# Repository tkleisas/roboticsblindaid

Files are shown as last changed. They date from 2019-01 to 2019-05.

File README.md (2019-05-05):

# roboticsblindaid
Σύστημα Ειδοποίησης Ατόμων με Προβλήματα Όρασης

Πρωτότυπο #1

Παρουσίαση του Project με βίντεο
================================
https://www.youtube.com/watch?v=oLjfnk1CDiU

Υλικά
=====
1. Αισθητήρας Υπερήχων HC-SR04 https://grobotronics.com/ultrasonic-sensor-sr04.html
2. Βύσματάκι για ακουστικά 3.5mm https://grobotronics.com/audio-jack-stereo-3.5mm-pcb.html
3. 2 ή περισσότερα micro:bit https://grobotronics.com/bbc-micro-bit-board.html
4. Boost converter για τη μετατροπή της τάσης από τα 3V που θα παρέχουν οι μπαταρίες στα 5V που απαιτεί ο αισθητήρας https://grobotronics.com/pololu-dc-dc-converter-step-up-5v-1.2a.html
5. Logic level converter για τη μετατροπή των τάσεων μεταξύ 3V και 5V έτσι ώστε να μπορούν να επικοινωνήσουν ο αισθητήρας υπερήχων που δουλεύει στα 5V με το microbit που δουλεύει στα 3V. https://grobotronics.com/logic-level-converter-bi-directional.html   
5. Μπαταριοθήκες https://grobotronics.com/battery-holder-2xa-with-jst-ph-connector.html
6. Perfboard για να συναρμολογήσουμε το κύκλωμά μας https://grobotronics.com/160x115mm.html
7. Μονόκλωνο καλώδιο σε διάφορα χρώματα για να κάνουμε τις συνδέσεις https://grobotronics.com/prototyping/hook-up-wires/
8. Pin header για την προσαρμογή του αισθητήρα υπερήχων στην πλακέτα! https://grobotronics.com/pin-header-1x40-female-2.54-mm.html
Προαιρετικά:
μοτέρ και Motor Driver Board για ειδοποίηση με δόνηση

Το σύστημα αυτό θα βοηθήσει τους ανθρώπους που έχουν προβλήματα όρασης να δουν τα εμπόδια που είναι πιο ψηλά από το μπαστούνι που έχουν για να κινηθούν. Μπορούμε να έχουμε αισθητήρες στο στήθος και στο κεφάλι (σε καπέλο) Ο αισθητήρας υπερήχων όταν ανιχνεύει κάποιο εμπόδιο θα κάνει τα ακουστικά να παράγουν έναν προειδοποιητικό ήχο, ώστε ο χρήστης του συστήματος να καταλάβει ότι έχει κάποιο εμπόδιο μπροστά του. Επίσης θα μπορούσαμε να χρησιμοποιήσουμε και κάποιο μοτέρ για ειδοποίηση. Θα χρησιμοποιηθούν 2 micro:bit, το ένα θα ανιχνεύει την κίνηση και θα στέλνει ασύρματα μήνυμα στο άλλο για να παράγει την ειδοποίηση. Τρόποι ειδοποίησης μπορεί να είναι τονικό ύψος του ήχου ανάλογα με την απόσταση ή επαναλήψεις του ήχου αντιστρόφος ανάλογες της απόστασης, ή κάποια μελωδία ή κάποια δόνηση παραγόμενη από το μοτέρ

Μπορούμε να δούμε στο επόμενο διάγραμμα μια ενδεικτική υλοποίηση ενός τέτοιου συστήματος που περιλαμβάνει μπαταρίες, ένα micro:bit, έναν αισθητήρα υπερήχων και έναν DC - DC boost converter. Επειδή το micro:bit θέλει 3 Volts, ενώ ο αισθητήρας χρειάζεται 5 Volts, χρησιμοποιούμε τον boost converter για να πάρουμε 5 Volts από τις δυο μπαταρίες ΑΑΑ που δίνουν 3 Volts. Με αυτό τον τρόπο μπορούμε να κάνουμε πιο μικρό και πιο ελαφρύ το κύκλωμά μας, πράγμα που είναι απαραίτητο για μια συσκευή που πρέπει να φοριέται. Θα μπορούσαμε να χρησιμοποιήσουμε ακόμη και μια μικρή, στρογγυλή μπαταρία λιθίου 3V (πχ CR2032) για ακόμη πιο μικρή συσκευή. Τέλος υπάρχει και ένα 3.5 mm jack στο οποίο μπορούμε να συνδέσουμε ακουστικό ώστε να έχουμε ηχητική ειδοποίηση.
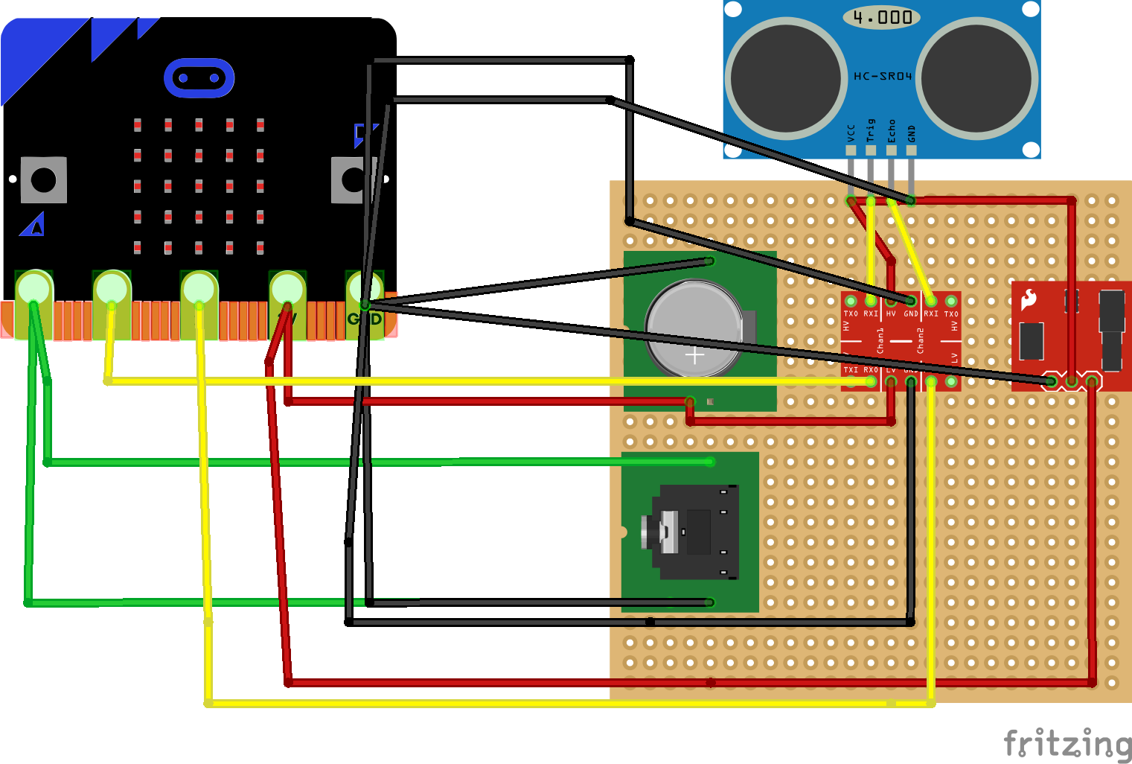
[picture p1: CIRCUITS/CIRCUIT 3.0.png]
Micro:bit and ultrasonic sensor

Μπορείτε να δείτε επίσης μερικές φωτογραφίες από την δοκιμαστική υλοποίηση που κάναμε.
Πλακέτα από πάνω

Πλακέτα από κάτω

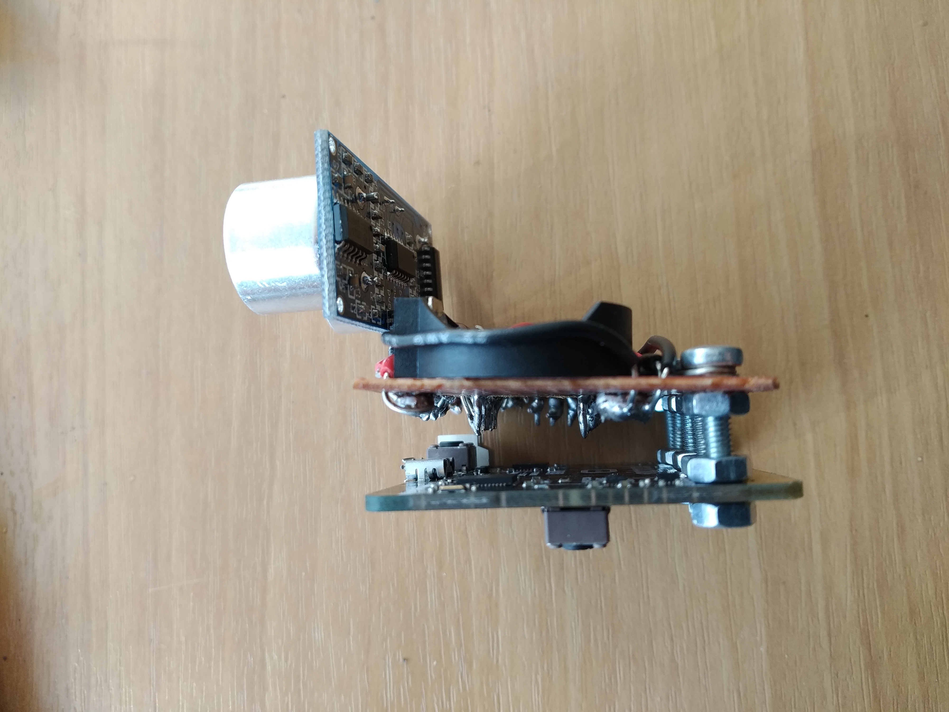
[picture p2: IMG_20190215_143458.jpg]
Πλακέτα από πλάϊ


Στον πάγκο εργασίας

Πατήστε εδώ για να δείτε το βίντεο με το πρωτότυπο.
https://youtu.be/QQmOa1Lk4nE

Επίσης στο φάκελο 3dprint μπορείτε να βρείτε σχέδια για ένα περίβλημα της συσκευής που σχεδιάσαμε στο openscad

Λίγα λόγια για την υλοποίηση του έργου
======================================

Στο κέντρο ρομποτικής και προγραμματισμού Καλαμάτας (που στελεχώνεται από εθελοντές εκπαιδευτικούς του Δημόσιου Σχολείου) ξεκινήσαμε φέτος μια σειρά μαθημάτων πάνω στις ανοιχτές τεχνολογίες.
Σκοπός μας ήταν να ξεκινήσουμε με το micro:bit και να συνεχίσουμε με Arduino και Raspberry pi. Όταν ανακοινώθηκε ο διαγωνισμός εκπαιδευτικής ρομποτικής και physical computing ανοιχτών τεχνολογιών της ΕΛΛΑΚ είχαμε σχεδόν ολοκληρώσει μια εισαγωγική σειρά μαθημάτων στο micro:bit και αποφασίσαμε να προτείνουμε ένα έργο που βρήκαμε ενδιαφέρον. Μια συσκευή ειδοποίησης ατόμων με προβλήματα όρασης. Το θέμα αυτό ήταν ελκυστικό γιατί αναφερόταν σε ένα υπαρκτό πρόβλημα, ενώ παράλληλα μπορεί να ευαισθητοποιήσει και να κινητοποιήσει τους μαθητές να καταλάβουν τα προβλήματα κάποιων συνανθρώπων τους και να προσπαθήσουν να τους βοηθήσουν. Παράλληλα μέσα από την ενασχόλησή τους αυτή, θα είχαν την ευκαιρία να γνωρίσουν κάποιες βασικές αρχές του physical computing, του προγραμματισμού, να σχεδιάσουν μια κατάλληλη διεπαφή έτσι ώστε οι χρήστες να μπορούν να χρησιμοποιήσουν τη συσκευή κ.ο.κ.

Αφού κάναμε αρκετές συζητήσεις για το πως θα μπορούσε να δουλέψει μια συσκευή και τους περιορισμούς που θα μπορούσε να έχει, δοκιμάσαμε μια αρχική υλοποίηση σε breadboard ενός κυκλώματος που περιελάμβανε έναν αισθητήρα υπερήχων, ένα micro:bit και τροφοδοσία του αισθητήρα από 4 επαναφορτιζόμενες μπαταρίες των 1,2 Volt (4,8 Volt) και ξεχωριστή τροφοδοσία για το micro:bit. Είδαμε ότι η χρήση 2 πηγών τροφοδοσίας δεν ήταν πρακτική και το σύστημα που προέκυπτε ήταν μεγάλο. Έτσι στη συνέχεια αποφασίσαμε να δούμε τη δυνατότητα να χρησιμοποιήσουμε ένα πιο απλό σχήμα τροφοδοσίας. Τελικά αποφασίσαμε να χρησιμοποιήσουμε έναν DC boost converter, ο οποίος θα έπαιρνε μια τάση τροφοδοσίας 3 Volts του micro:bit και θα την ανέβαζε στα 5 που χρειαζόταν για να δουλέψει ο αισθητήρας υπερήχων. Όμως είδαμε ότι η τάση που έστελνε το micro:bit για να κάνει τον αισθητήρα να στείλει τον υπερηχητικό παλμό μερικές φορές δεν τον ενεργοποιούσε. Παράλληλα χρησιμοποιούσαμε έναν διαιρέτη τάσης στο pin εξόδου για να μετατρέψουμε τα 5 volts που γύρναγε ο αισθητήρας σε 3V έτσι ώστε να μην υπάρχει πρόβλημα με το micro:bit. Έτσι τελικά αποφασίσαμε να χρησιμοποιήσουμε έναν logic level converter, ο οποίος μας επέτρεψε να δουλέψουμε χωρίς πρόβλημα καθώς έκανε δυνατή την μετατροπή των τάσεων από τα 3Volts στα 5Volts και αντίστροφα. Με αυτές τις αλλαγές το κύκλωμά μας δούλευε. Όμως επειδή ήταν σε breadboard ήταν πολύ εύθραυστο και δεν θα μπορούσε να χρησιμοποιηθεί για τη δημιουργία ενός πρωτοτύπου. Για αυτό το λόγο αποφασίσαμε να φτιάξουμε το σύστημά μας σε πλακέτα (perfboard) και να συνδέσουμε τα διάφορα μέρη με καλώδια. Οι μαθητές είδαν τη διαδικασία της κόλλησης σε μια πλακέτα με κολλητήρι και δοκίμασαν κάποιες απλές κολλήσεις. Όμως τελικά το πρωτότυπο κατασκευάστηκε στο εργαστήριό μας. Το πρώτο - πρώτο που φτιάχτηκε δε δούλεψε καν. Στη συνέχεια όμως η δεύτερη δοκιμή ήταν επιτυχημένη.

Προγραμματίσαμε τη συσκευή στο περιβάλλον make:code. Ο προγραμματισμός έγινε από τους μαθητές, οι οποίοι χρησιμοποίησαν και διαφορετικούς ήχους προκειμένου να βοηθήσουν το χρήστη να ρυθμίσει την απόσταση ειδοποίησης της συσκευής.

Στο μεταξύ η πρότασή μας πήρε χρηματοδότηση από την ΕΛΛΑΚ, οπότε μπορέσαμε να φτιάξουμε άλλα 3 πρωτότυπα, εφαρμόζοντας αυτά που μάθαμε από το πρώτο πρωτότυπο. Στη συνέχεια έπρεπε να βάλουμε την πλακέτα μας σε ένα κουτί. Για το σκοπό αυτό διαθέταμε έναν επιτραπέζιο εκτυπωτή PrimaCreator p120 v3. Αρχικά είπαμε κάποια πράγματα για την τρισδιάστατη εκτύπωση και το πως δουλεύει και στη συνέχεια δοκιμάσαμε να σχεδιάσουμε ένα κουτί στο tinkercad. Το τελικό κουτί φτιάχτηκε με το πρόγραμμα OpenScad το οποίο έχει το πλεονέκτημα ότι είναι open source και ότι φτιάχνει τρισδιάστατα μοντέλα με μια γλώσσα προγραμματισμού! Αφού σχεδιάσαμε το κουτί, κάναμε μια δοκιμαστική εκτύπωση, διορθώσαμε κάποιες διαστάσεις και κάναμε μια εκτύπωση του κουτιού. Παρόλες τις διορθώσεις, υπήρχαν μερικά προβλήματα που διορθώθηκαν με λίμα και γυαλόχαρτο. Οι μαθητές δεν είδαν την διαδικασία εκτύπωσης ζωντανά, αλλά από βίντεο και timelapse,
γιατί ο εκτυπωτής δεν ήταν στο χώρο που κάναμε μάθημα. Η εκτύπωση της θήκης πήρε γύρω στις 18 ώρες και την έχουμε τεκμηριώσει με σχετικά βίντεο.

Στη συνέχεια κουμπώσαμε τη συσκευή μας στο κουτί και κάναμε κάποιες δοκιμές. Η συσκευή μας δουλεύει, χρειάζεται όμως δουλειά πάνω στην εργονομία, πράγμα που διαπιστώσαμε και με τις δοκιμές. Κάτι που παραλείψαμε είναι ένα ρυθμιστικό της έντασης ειδοποίησης της συσκευής και ενδεχομένως κάποιο ενσωματωμένο ηχείο, έτσι ώστε να μη χρειάζονται ακουστικά.

Δεν προλάβαμε να υλοποιήσουμε την χρήση περισσότερων από ένα micro:bit για την ειδοποίηση. 

Στο μέλλον θα θέλαμε να εξετάσουμε και τη χρήση άλλων πλατφορμών, όπως το Arduino για την υλοποίηση της συσκευής μας, καθώς και το ενδεχόμενο η συσκευή μας να επικοινωνεί με το κινητό του χρήστη και να συνδιάζει και πληροφορίες από το κινητό για να τον βοηθάει να κινηθεί.

Τα μέλη της ομάδας μας είναι (αλφαβητικά):

Παναγιώτης Ξαρχάκος
Γιώργος Κωνσταντόπουλος
Γιώργος Τριανταφυλλάκης

Εμψυχωτές - συμβουλάτορες:

Τάσος Κλείσας
Παναγιώτης Μελιγαλιώτης
Βασίλης Μιχαλόπουλος

Διάθεση του περιεχομένου
========================

Ο κώδικας του έργου διατίθεται με άδεια GPL v3.0

Το περιεχόμενο του έργου διατίθεται με άδεια Creative Commons Αναφορά Δημιουργού 4.0 Διεθνές.

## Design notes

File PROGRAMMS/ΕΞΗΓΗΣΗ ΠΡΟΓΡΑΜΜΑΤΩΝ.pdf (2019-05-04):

### ΕΞΗΓΗΣΗ ΠΡΟΓΡΑΜΜΑΤΩΝ

ΧΡΟΝΟΛΟΓΙΚΗ ΣΕΙΡΑ
BEEPER

Ένα απλό πρόγραμμα που ο ήχος που παράγεται μοιάζει με beeper από αυτοκίνητο όταν κάνει όπισθεν. Έχουμε μία μεταβλητή, η οποία μπορεί να αυξομειωθεί από τα κουμπιά Α και Β του micro:bit και ανάλογα την τιμή της μεταβλητής παράγεται ο αντίστοιχος ήχος.

PROGRAMM 1.0

Το πρόγραμμα αυτό παίρνει τιμές από έναν ultrasonic sensor και μας παρουσιάζει την τιμή στην οθόνη του micro:bit.

PROGRAMM 2.0

Σε αυτό το πρόγραμμα το micro:bit δείχνει με την βοήθεια της επέκτασης greek-led beta και Sonar στην LED 5*5 οθόνη του την μέση τιμή 5 τιμών που παίρνει ο αισθητήρας υπερήχων

PROGRAMM 3.0

Ενώσαμε λοιπόν το πρόγραμμα BEEPER με το PROGRAMM 2.0, ώστε να αναπαράγεται ήχος ανάλογα με το τι βλέπει ο αισθητήρας και όχι ότι του βάζουμε εμείς πατώντας τα κουμπιά Α και Β.

PROGRAMM NOTES 1.0

Ο Ultrasonic Sensor μετράει την απόσταση την οποία δείχνει στην οθόνη LED του micro:bit και αν η τιμή βρίσκεται ανάμεσα στις τιμές 100 και 80 θα παίζει μία νότα, όταν είναι ανάμεσα σε 80 και 60 μία πιο ψηλή νότα, κοκ.

PROGRAMM NOTES 2.0

Παρατηρήσαμε ότι οι τιμές που βγάζει στην οθόνη το micro:bit δεν είναι σταθερές και για να σταθεροποιήσουμε αυτή τη τιμή φτιάξαμε μία συνάρτηση με την οποία ο Ultrasonic Sensor θα παίρνει πολλές τιμές και στην οθόνη θα δείχνει μία μέση τιμή, αυτό θα βοηθήσει και στην καλύτερη ειδοποίηση του ατόμου με το πρόβλημα όρασης

PROGRAMM NOTES 2.1

Σκεφτήκαμε πως τα άτομα με προβλήματα όρασης μπορεί να μην θέλουν να ειδοποιούνται από τα 100 cm αλλά από τα 80 ή από τα
200. Αυτό το καταφέραμε ρωτώντας στην αρχή τον χρήστη να μας δώσει μία τιμή, την οποία ο χρήστης μπορεί να αυξομειώσει με τα κουμπιά Α και Β. Όμως, επειδή οι χρήστες δεν θα μπορούν να βλέπουν τον αριθμό στην οθόνη, κάθε φορά που αλλάζει αυτός ο αριθμός θα ακούγεται ένα beat ανάλογα την τιμή που δίνεται (10cm 1 beat, 20cm 2 beat, κοκ).

PROGRAMM NOTES 2.2

Το micro:bit θα μπορεί πια να στέλνει την τιμή που παίρνει ο αισθητήρας υπερήχων σε μία οθόνη LCD η οποία θα δείχνει τον ίδιο αριθμό που φαίνεται και στην 5Χ5 οθόνη του micro:bit που χρησιμοποιεί ο χρήστης. Την οθόνη αυτή την χρησιμοποιούμε εμείς για να βλέπουμε τι τιμές παίρνει το micro:bit χωρίς να χρειάζεται να κοιτάμαι την οθόνη του χρήστη. Το πρόγραμμα που λαμβάνει την τιμή και το οποίο περνάμε στο micro:bit της LCD οθόνης έχει όνομα: "PROGRAMM NOTES LCD EDITION"

PROGRAMM LCD EDITION

Αυτό το πρόγραμμα το περνάμε στο micro:bit που έχει την LCD οθόνη. Με τη βοήθειά του λαμβάνει την τιμή που στέλνει το άλλο micro:bit.

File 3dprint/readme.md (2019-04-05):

Σε αυτό το φάκελο μπορείτε να βρείτε ένα σχέδιο περιβλήματος για την κατασκευή μας. Το σχέδιο έγινε με το λογισμικό ανοιχτού κώδικα openscad.
Ουσιαστικά είναι ένα πρόγραμμα το οποίο μπορεί να παράξει αρχεία STL τα οποία μπορούμε να εκτυπώσουμε αφού πρώτα τα εισάγουμε σε ένα πρόγραμμα slicer, όπως για παράδειγμα το CURA

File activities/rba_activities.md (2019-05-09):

Robotics Blind Aid
Περίγραμμα εκπαιδευτικών σεναρίων

1.	Εισαγωγή. Η σκοτεινή χώρα.

Για κάποιους συνανθρώπους μας η αίσθηση της όρασης απουσιάζει ή είναι πολύ περιορισμένη. Κάποιοι γεννήθηκαν έτσι, σε κάποιους έτυχε κατά τη διάρκεια της ζωής τους. Θα μπορούσε να συμβεί στον καθένα μας. Φυσικά οι άνθρωποι αυτοί ζουν με το πρόβλημά τους. Έχουν μάθει να εκμεταλλεύονται τις υπόλοιπες αισθήσεις τους με σκοπό να μπορούν να λειτουργήσουν στην κοινωνία. Πολλοί από αυτούς εργάζονται κανονικά. Πως είναι όμως να ζει κάποιος με πρόβλημα όρασης;

Βιωματική δραστηριότητα.
Δένουμε τα μάτια των μαθητών και τους αφήνουμε να περιπλανηθούν στον χώρο που περιέχει διάφορα εμπόδια (καρέκλες, θρανία κλπ). Αφού δοκιμάσουν όλοι, τους δίνουμε ένα μπαστούνι. Συζητάμε για το αν ήταν πιο εύκολη ή πιο δύσκολη η κίνηση με το μπαστούνι. Συζητάμε για τα πλεονεκτήματα και τα μειονεκτήματα του μπαστουνιού και τις εναλλακτικές που τυχόν γνωρίζουμε (πχ. Σκύλος οδηγός τυφλών). Συζητάμε για το πως η τεχνολογία μπορεί να βοηθήσει άτομα που αντιμετωπίζουν προβλήματα υγείας. Για παράδειγμα, η σύνθεση φωνής που χρησιμοποιούσε ο Stephen Hawking και του επέτρεπε να επικοινωνεί παρόλη την πάθηση (ALS) από την οποία έπασχε.

2.	Physical computing. Οι υπολογιστές αντιλαμβάνονται τον κόσμο.

Εμείς οι άνθρωποι διαθέτουμε αισθήσεις με τις οποίες αντιλαμβανόμαστε τον κόσμο. Με αυτές τις αισθήσεις, βρίσκουμε το δρόμο μας, αναζητούμε τροφή, μαθαίνουμε καινούρια πράγματα, προφυλασσόμαστε από τον κίνδυνο. Δεν υπάρχει ανθρώπινη δραστηριότητα στην οποία να μην εμπλέκονται μία ή περισσότερες αισθήσεις. Οι υπολογιστές μπορούν άραγε να αποκτήσουν αισθήσεις και να αντιληφθούν το περιβάλλον;
Συζήτηση με τους μαθητές. Παραδείγματα.
Οι υπολογιστές μπορούν να εξοπλιστούν με αισθητήρες. Ένας αισθητήρας μπορεί εκμεταλλευόμενος τους νόμους της φυσικής να αντιληφθεί φυσικά μεγέθη και να τα μετατρέψει σε αριθμούς κατάλληλους για επεξεργασία από έναν υπολογιστή. Παραδείγματα: επιταχυνσιόμετρο κινητού, συναγερμός, αισθητήρας παρκαρίσματος. Θα μπορούσαμε να χρησιμοποιήσουμε έναν ή περισσότερους αισθητήρες για να βοηθήσουμε άτομα με προβλήματα όρασης να αντιληφθούν καλύτερα το περιβάλλον τους.

3.	Micro:bit, ένας υπολογιστής με πολλές δυνατότητες.
Το micro:bit είναι ένας υπολογιστής σε μορφή πλακέτας ο οποίος διαθέτει πολλές δυνατότητες. Μπορεί να συνδεθεί εύκολα με αισθητήρες και μας επιτρέπει να φτιάξουμε διασκεδαστικές εφαρμογές όπως παιχνίδια, χρήσιμα εργαλεία (π.χ. πυξίδα), ρομποτικά οχήματα κ.ο.κ. Στο micro:bit μπορούμε να ξεκινήσουμε με δραστηριότητες όπως αυτές που περιγράφονται εδώ:
 https://4dimkal-robot.weebly.com/epsilonkappapialphaiotadeltaepsilonupsilontauiotakappa941sigmaf-deltarhoalphasigmatauetarhoiota972tauetatauepsilonsigmaf.html 
ή εδώ:
http://giamiaxoufta.blogspot.com/2018/10/microbit.html
Με σκοπό να εξοικειωθούν οι μαθητές με το micro:bit

4.	Σύνδεση ενός αισθητήρα υπερήχων με το micro:bit.
 Ο αισθητήρας υπερήχων μας επιτρέπει να μετράμε απόσταση. Δουλεύει στέλνοντας έναν υπερηχητικό παλμό ο οποίος αν συναντήσει εμπόδιο αντανακλάται και επιστρέφει πίσω. Ό χρόνος που μεσολαβεί από τη στιγμή που στείλουμε τον παλμό μέχρι τη στιγμή που θα ανιχνεύσουμε την αντανάκλασή του αντιστοιχεί στο διπλάσιο της  απόστασης από το αντικείμενο. Γνωρίζοντας και την ταχύτητα του ήχου στον αέρα μπορούμε να προσδιορίσουμε την απόσταση από το εμπόδιο. Με αυτό τον τρόπο λειτουργούν και τα δελφίνια και οι νυχτερίδες και γενικότερα όλα τα πλάσματα που χρησιμοποιούν ηχοεντοπισμό. Αντίστοιχα τέτοιες διατάξεις χρησιμοποιούμε στα σόναρ, τους αισθητήρες παρκαρίσματος κ.ο.κ. Βλέπουμε έναν τέτοιον αισθητήρα (HC-SR04) και ανακαλύπτουμε πως δουλεύει. Προσπαθούμε να τον συνδέσουμε με το micro:bit και ανακαλύπτουμε ότι ο συγκεκριμένος έχει κάποιες απαιτήσεις σε τάση που δεν μπορούν να καλυφθούν από το micro:bit. Δοκιμάζουμε πάντως τη σύνδεση με το micro:bit και έναν διαιρέτη τάσης για να μετατρέψουμε την τάση που επιστρέφει ο αισθητήρας από 5Volt σε 3Volt. Εξηγούμε την πολύπλοκη συνδεσμολογία μπαταρίας που απαιτείται.
5.	Σύνδεση ενός αισθητήρα υπερήχων μέρος β

6.	Προγραμματισμός του αισθητήρα για ειδοποίηση

7.	Πλακέτες

8.	Κουτί – 3D printing μέρος 1

9.	Κουτί – 3D printing μέρος 2

10.	Δοκιμές του συστήματος

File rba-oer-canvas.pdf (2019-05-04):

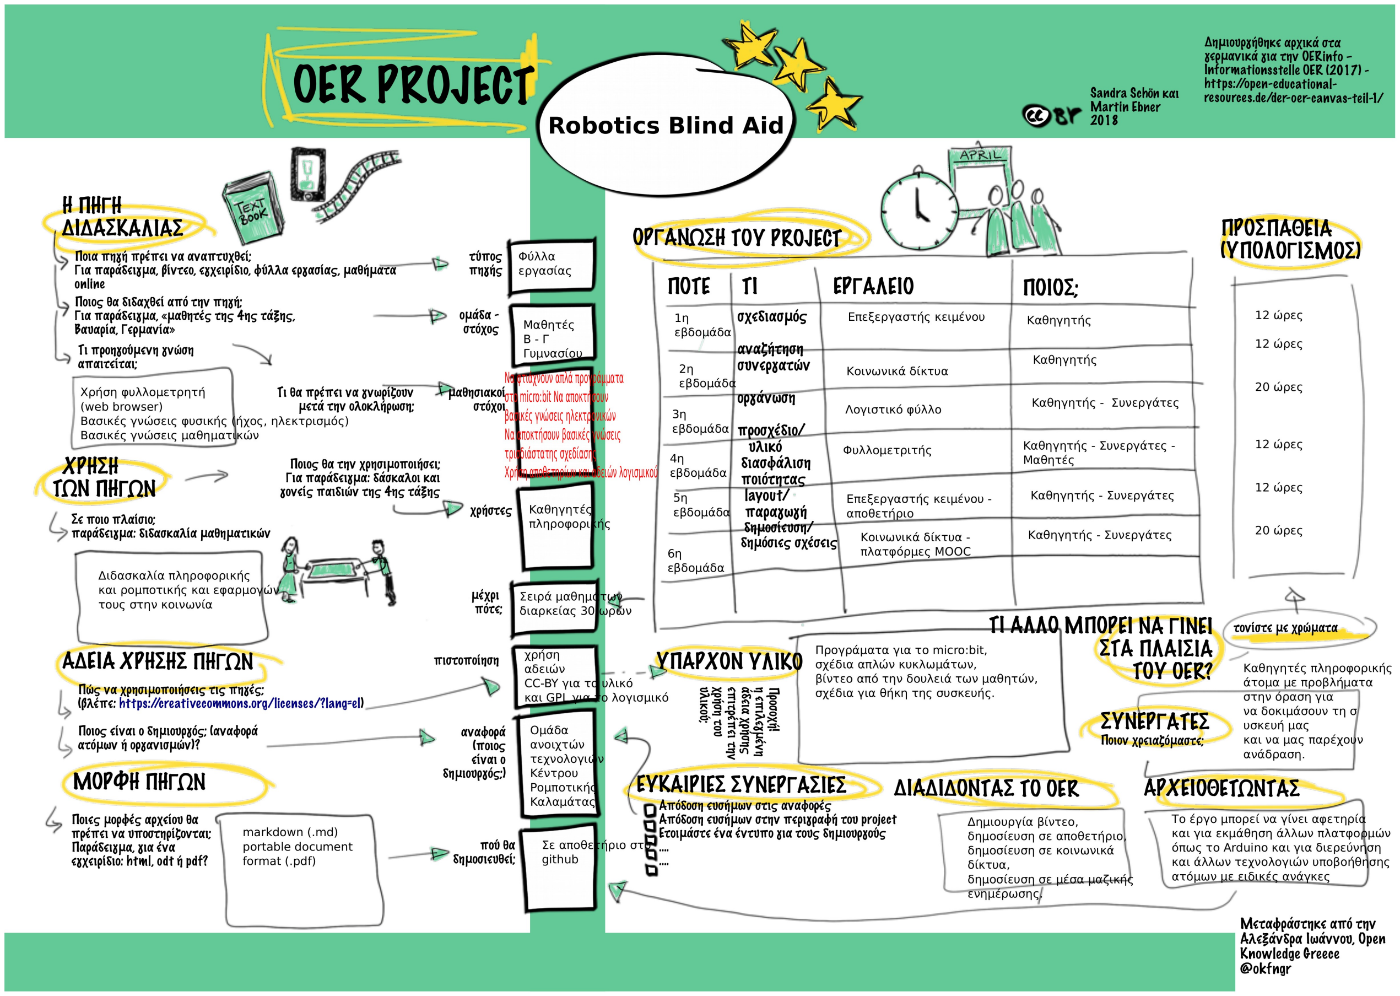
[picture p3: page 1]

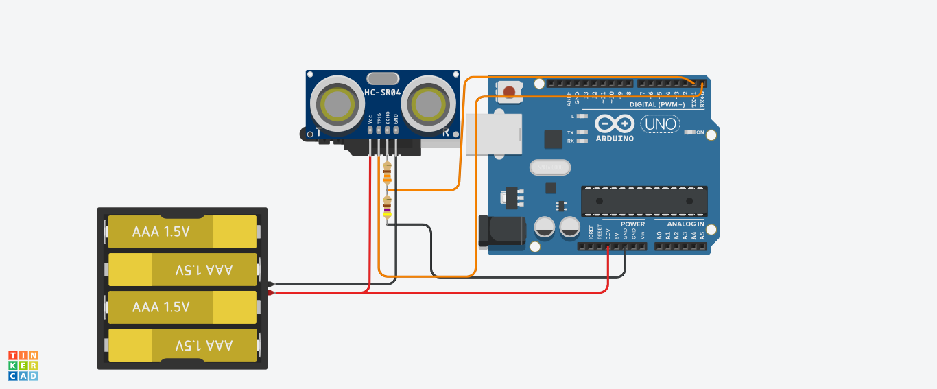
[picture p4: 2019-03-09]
CIRCUITS/CIRCUIT 1.0.png

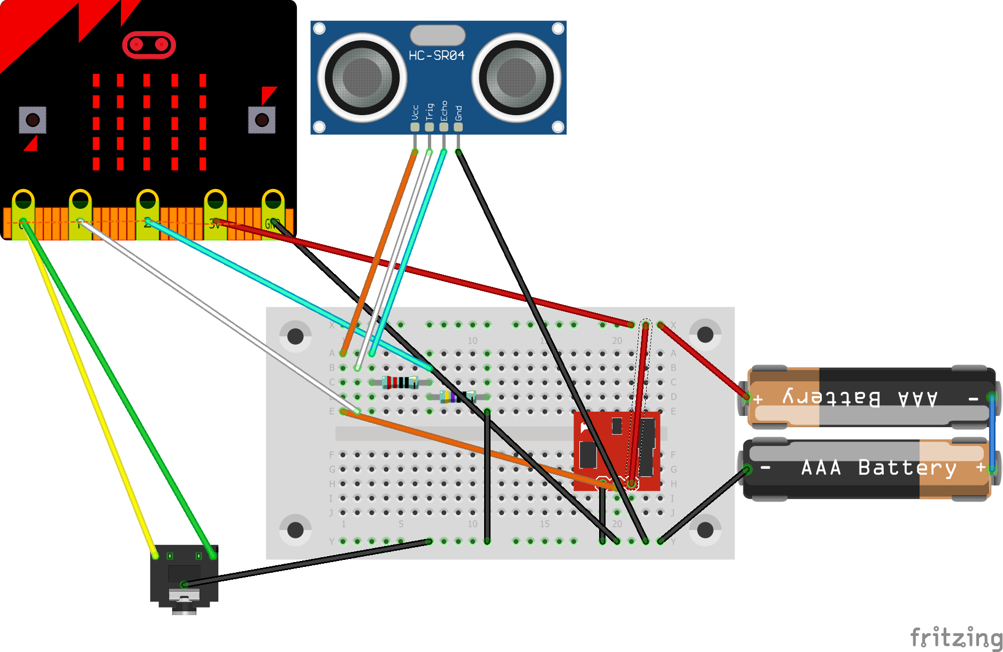
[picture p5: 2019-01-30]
CIRCUITS/CIRCUIT 2.0.png

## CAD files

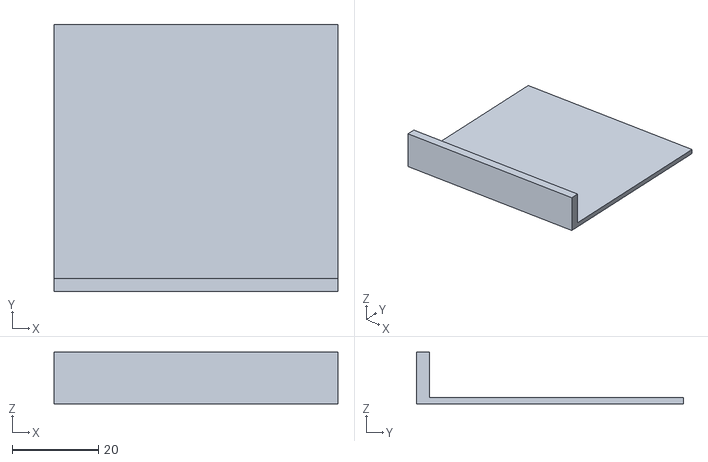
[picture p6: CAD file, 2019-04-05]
3dprint/rba3_lid.stl
66.0 x 62.0 x 12.0

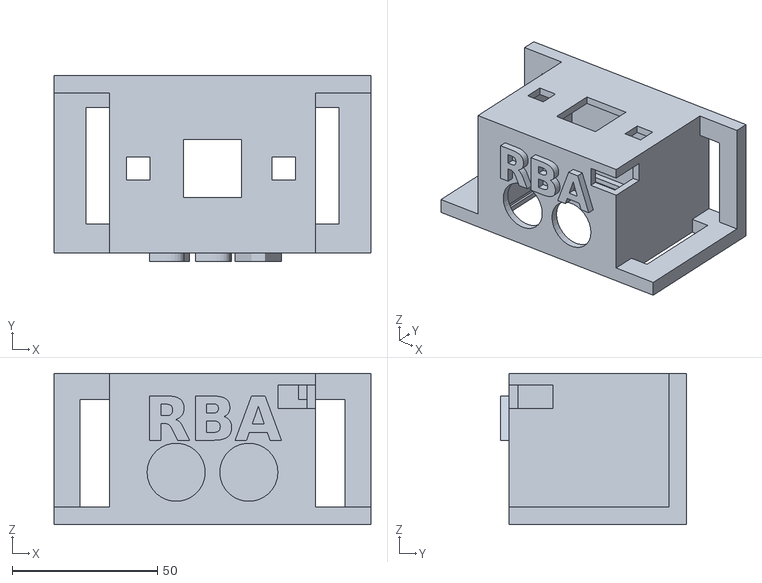
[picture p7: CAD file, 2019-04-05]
3dprint/rba2.stl
109.0 x 64.0 x 52.0

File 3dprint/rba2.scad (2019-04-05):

$w=65; //width in mm
$h=46; // height in mm
$d=52; // depth in mm
$l=3; // thickness
$sw=20; //screen window width
$sh=20; //screen window height
$bw=8; // button window width
$bh=8; // button window height
union()
{
    cube([66,59+$l,1.5]);
    cube([66,$l,4*$l]);
}
/*
difference()
{
    union()
    {
        union()
        {
            difference()
            {
                cube([$w+2*$l,$l,$h+2*$l]);
                translate([$l+20,2*$l,15+$l])
                {
                    rotate([90,0,0])
                    {
                        cylinder(4*$l,r=10);
                    }
                }
                translate([$l+20+25,2*$l,15+$l])
                {
                    rotate([90,0,0])
                    {
                        cylinder(4*$l,r=10);
                    }
                }
            }
            
            
            color([0,0,0,1])
            {
                translate([4*$l, $l,29])
                {
                    rotate([90,0,0])
                    {
                        linear_extrude(height=2*$l)
                        {
                            text("RBA", size=15,font=str("Arial Black",":style=Bold"));
                        }
                    }
                }
            }
        }
        difference()
        {
            cube([$l,$d+2*$l,$h+2*$l]);
        }
        difference()
        {
            translate([$w+$l,0,0])
            {
                cube([$l,$d+2*$l,$h+2*$l]);
            }
        }
        difference()
        {
            translate([0,$d+2*$l,0])
            {
                cube([$w+2*$l,$l,$h+2*$l]);
            }
        }
        difference()
        {
            translate([0,0,$h+$l])
            {
                cube([$w+2*$l,$d+2*$l,$l]);
            }
            translate([($w-$sw)/2+$l,($d-$sh)/2+$l,$h-$l])
            {
                cube($sw,$sh,3*$l);
            }
            translate([$l+3,($d-$bh)/2+$l,$h-$l])
            {
                cube([$bw,$bh,3*$l]);
            }
            translate([$w-3*$l,($d-$bh)/2+$l,$h-$l])
            {
                cube([$bw,$bh,3*$l]);
            }
        }
        difference()
        {
            translate([-15-$l-1,0,0])
            {
                cube([15+$l+1,$d+3*$l,2*$l]);
            }
            translate([-8,10,0])
            {
                cube([5+$l,$d-4*$l,2*$l]);
            }
        }
        difference()
        {
            translate([$w+2*$l,0,0])
            {
                cube([15+$l+1,$d+3*$l,2*$l]);
            }
            translate([$w+5*$l-9,10,0])
            {
                cube([5+$l,$d-4*$l,2*$l]);
            }
        }
        */
        /*
        difference()
        {
            translate([$w+2*$l,$d+$l,0])
            {
                cube([15+$l+1,2*$l,$h+2*$l]);
            }
            translate([$w+2*$l,$d+$l,0])
            {
                cube([5+$l+5,2*$l,$h-2*$l]);e
            }
        }
        */
        /*
        union()
        {
            translate([$w+16,$d+$l,0])
            {
                cube([5+$l+1,2*$l,$h+2*$l]);
            }
            translate([$w,$d+$l,$h-$l])
            {
                cube([15+$l+1,2*$l,3*$l]);
            }
        }
        union()
        {
            translate([-15-$l-1,$d+$l,0])
            {
                cube([5+$l+1,2*$l,$h+2*$l]);
            }
            translate([-8-$l,$d+$l,$h-$l])
            {
                cube([15+$l+1,2*$l,3*$l]);
            }
        }
    }

    translate([$l-1,$l-1,$l-1])
    {
        cube([$w+2,$d+3*$l,$l-1]);
    }
    translate([$w-10+$l,0,40])
    {
        cube([15,15,8]);
    }

}
*/

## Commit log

2018-12-13 PROGRAMM 2.0
    Σε αυτό το πρόγραμμα το BBC micro:bit δείχνει με την βοήθεια της επέκτασης greek-led beta και Sonar στην LED 5*5 οθόνη του την μέση τιμή 5 τιμών που παίρνει ο αισθητήρας υπερήχων
    Link for the greek - led beta: https://github.com/tkleisas/pxt-greekled-beta
2018-12-13 PROGRAMM 1.0
    Σε αυτό το πρόγραμμα το Microbit μας δείχνει τιμές που παίρνει ο αισθητήρας υπερήχων. (ΟΧΙ ΑΚΡΙΒΕΣ - βλ. PROGRAMM 2.0)
2018-12-13 BEEPER
    Σε αυτό το πρόγραμμα το Microbit αναπαράγει έναν ήχο ανάλογα με την μεταβλητή distance την οποία μεταβάλουμε με την βοήθεια των κουμπιών A και B
2018-12-26 PROGRAMM 3.0
    Χρόνια πολλά και καλές γιορτές σε όλους! Ένωσα λοιπόν το πρόγραμμα BEEPER με το PROGRAMM 2.0 αφού πιστεύω πως χρειαζόταν, ώστε να αναπαράγεται ήχος ανάλογα με το τι βλέπει ο αισθητήρας και όχι ότι το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
2018-12-26 BEEPER
    Τελική μορφή προγράμματος beeper (ελπίζω)!!! Πρόσθεσα μία ακόμα εντολή. Το τσέκαρα και δουλεύει!
2019-01-30 Σχηματικό διάγραμμα αισθητήρα υπερήχων
    Ένα σχηματικό διάγραμμα σύνδεσης ενός αισθητήρα υπερήχων με το micro:bit που μπορεί να παράξει ηχητική ένδειξη
2019-01-30 Ενημέρωση με σχηματικό διάγραμμα
2019-02-19 CIRCUIT 3.0
    Στο σχέδιο βλέπουμε πως χρησιμοποιούμε ένα Perfboard πάνω στο οποίο βάζουμε όλα τα εξαρτήματα που θα χρειαστούμε
    (1x 3V Battery, 1x 3.5mm Jack, 1x DC - DC Boost Converter, 1x Level Converter και 1x Ultrasonic Sensor HC-SR04)
    Χρησιμοποιούμε την μπαταρία των 3V για να τροφοδοτήσουμε το micro:bit, τον Level και τον Boost Converter.
    Ο Level Converter μας βοηθά να μετατρέψουμε τις τάσεις που δίνει ο Ultrasonic από 5V σε 3V, ώστε να μπορέσει να "διαβάσει" τα δ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
    [CIRCUIT 3.0.fzz]
2019-03-06 Ενημέρωση της λίστας υλικών με links
2019-03-06 Προσθήκη φωτογραφιών από το πρωτότυπο
2019-03-06 Προσθήκη animated gif
2019-03-08 PROGRAMM NOTES 2.0
    Βάλαμε μέσα ένα function που θα παίρνει 5 τιμές και θα μας δίνει έναν μέσο όρο για να αποφύγουμε το να φαίνονται πολλές τιμές ταυτόχρονα στην οθόνη του Micro:bit. Το πρόγραμμα θα συνεχίσει να εξελίσσ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
2019-03-08 BEEPER
    Ένα απλό πρόγραμμα που ο ήχος που παράγεται μοιάζει με beeper από αυτοκίνητο όταν κάνει όπισθεν. Έχουμε μία μεταβλητή, η οποία μπορεί να αυξομειωθεί από τα κουμπιά Α και Β του micro:bit και ανάλογα τ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
2019-03-08 PROGRAMM 1.0
    Το πρόγραμμα αυτό παίρνει τιμές από έναν ultrasonic sensor και μας παρουσιάζει την τιμή στην οθόνη του micro:bit.
2019-03-08 PROGRAMM 2.0
    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
2019-03-08 PROGRAMM 3.0
    Ενώσαμε λοιπόν το πρόγραμμα BEEPER με το PROGRAMM 2.0 αφού πιστεύω πως χρειαζόταν, ώστε να αναπαράγεται ήχος ανάλογα με το τι βλέπει ο αισθητήρας και όχι ότι του βάζουμε εμείς πατώντας τα κουμπιά Α κ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
2019-03-09 PROGRAMM NOTES 1.0
    Ο Ultrasonic Sensor παίρνει μία τιμή την οποία δείχνει στην οθόνη LED του micro:bit και αν η τιμή βρίσκεται ανάμεσα στις τιμές 100 και 80 θα παίζει μία νότα, όταν είναι ανάμεσα σε 80 και 60 μία πιο ψ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
2019-03-09 PROGRAMM NOTES 2.0
    Παρατηρήσαμε ότι οι τιμές που βγάζει στην οθόνη το micro:bit δεν είναι σταθερές και για να σταθεροποιήσουμε αυτή τη τιμή φτιάξαμε μία συνάρτηση με την οποία ο Ultrasonic Sensor θα παίρνει πολλές τιμέ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
2019-03-09 CIRCUIT 1.0
    Επειδή το TinkerCAD δεν είχε micro:bit χρησιμοποιήσαμε ένα Arduino για το σχέδιο και επειδή δεν έχουν τα ίδια pins βάλαμε σχόλια σε κάθε pin που έχουμε βάλει καλώδια για να δείξουμε ποιο είναι το αντ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
2019-03-09 CIRCUIT 2.0
    Χρησιμοποιήσαμε το fritzing για να φτιάξουμε το κύκλωμα, διότι υπάρχει το micro:bit και όλα τα εξαρτήματα που χρειαζόμαστε. Μπορούμε να δούμε στο διάγραμμα αυτό μια ενδεικτική υλοποίηση ενός τέτοιου 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
2019-03-09 CIRCUIT 3.0
    [CIRCUIT 3.0.fzz]
2019-03-09 PROGRAMM NOTES 2.1
    Σκεφτήκαμε πως τα άτομα με προβλήματα όρασης μπορεί να μην θέλουν να ειδοποιούνται από τα 100 cm αλλά από τα 80 ή από τα 200. Αυτό το καταφέραμε ρωτώντας στην αρχή τον χρήστη να μας δώσει μία τιμή, τ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
2019-04-05 Προσθήκη αρχείων για τρισδιάστατη εκτύπωση
    [rba2.scad, rba2.stl, rba3_lid.stl]
2019-05-04 Προσθήκη OER CANVAS pdf του έργου
2019-05-04 Διορθώσεις και προσθήκες
2019-05-04 PROGRAMMS
    Τα ίδια προγράμματα που είναι ανεβασμένα σε αυτόν τον φάκελο σε JavaScript, αλλά στην μορφή .hex.
2019-05-04 PROGRAMM NOTES 2.2
    Οι αλλαγές που έχουν γίνει είναι ότι το micro:bit θα μπορεί πια να στέλνει την τιμή που παίρνει ο αισθητήρας υπερήχων σε μία οθόνη LCD η οποία θα δείχνει τον ίδιο αριθμό που φαίνεται και στην 5Χ5 οθό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
2019-05-04 PROGRAMM NOTES LCD EDITION
    Αυτό το πρόγραμμα το περνάμε στο micro:bit που έχει την LCD οθόνη. Με τη βοήθειά του λαμβάνει την τιμή που στέλνει το άλλο micro:bit.
2019-05-04 ΕΞΗΓΗΣΗ ΠΡΟΓΡΑΜΜΑΤΩΝ
    Σε αυτό το PDF εξηγούμε το τι κάνει κάθε πρόγραμμα που έχουμε ανεβάσει στο github.
2019-05-05 Προσθήκη βίντεο παρουσίασης του project
2019-05-05 Πληροφορίες για υλοποίηση - ομάδα
2019-05-05 Ενημέρωση αδειών χρήσης
2019-05-09 Εκπαιδευτικές δραστηριότητες
